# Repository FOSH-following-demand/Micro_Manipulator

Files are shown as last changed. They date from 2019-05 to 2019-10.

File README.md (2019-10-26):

# Micro Manipulator v2.0

Hi! we have a new design for the micromanipulator! check this out:

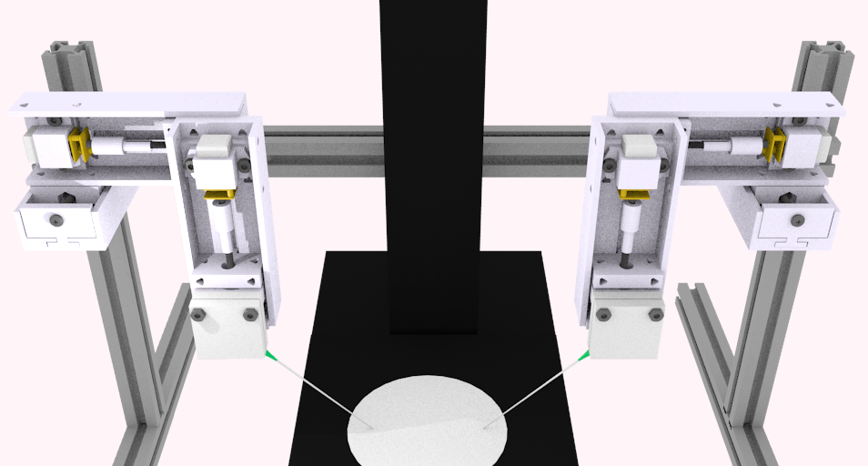
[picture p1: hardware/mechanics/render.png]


# 3D Printed parts

-Axis Base: This is the main component of each axis because it holds all other components.

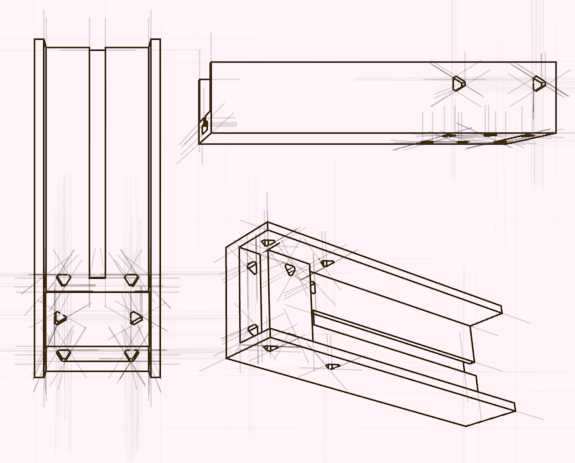
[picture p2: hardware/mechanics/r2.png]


You can find the STL file here: https://github.com/FOSH-following-demand/Micro_Manipulator/blob/master/hardware/mechanics/axis_base.stl

-Axis-Motor: It fixates the motor to the axis base

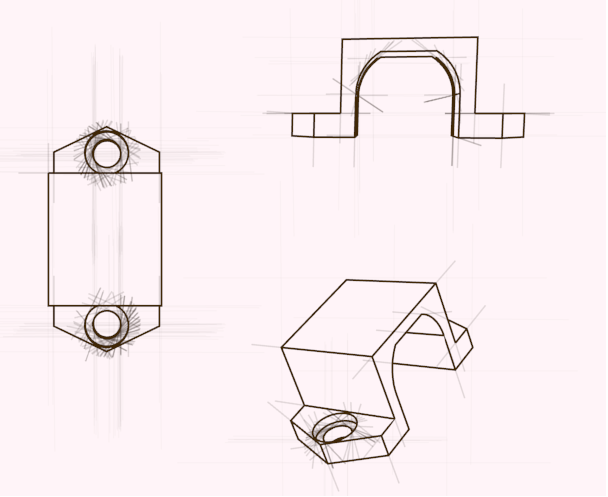
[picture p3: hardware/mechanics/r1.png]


You can find the STL file here: https://github.com/FOSH-following-demand/Micro_Manipulator/blob/master/hardware/mechanics/axis_motor.stl

-Axis TAP: The lid that closes the axis structure

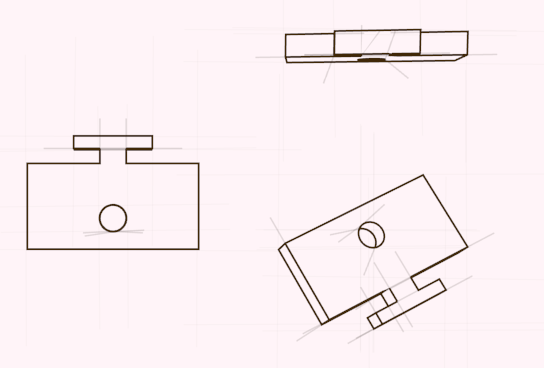
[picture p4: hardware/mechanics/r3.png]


You can find the STL file here: https://github.com/FOSH-following-demand/Micro_Manipulator/blob/master/hardware/mechanics/axis_tap.stl

-Axis Bolt A: One of the two pieces that when coupled turn rotational movement into linear one. 

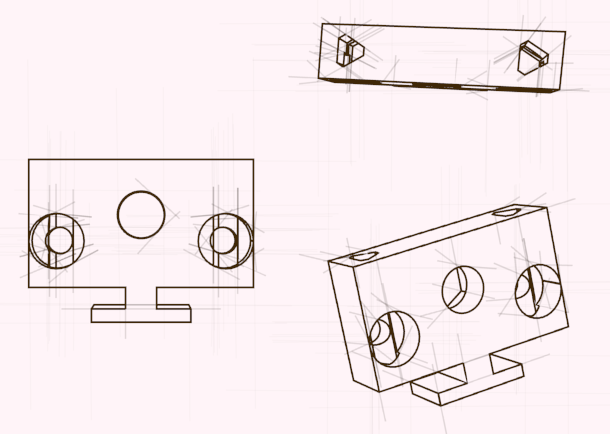
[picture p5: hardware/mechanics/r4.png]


You can find the STL file here: https://github.com/FOSH-following-demand/Micro_Manipulator/blob/master/hardware/mechanics/axis_bolt_a.stl

-Axis Bolt B: This piece complements axis bolt A to turn rotational movement into linear one 

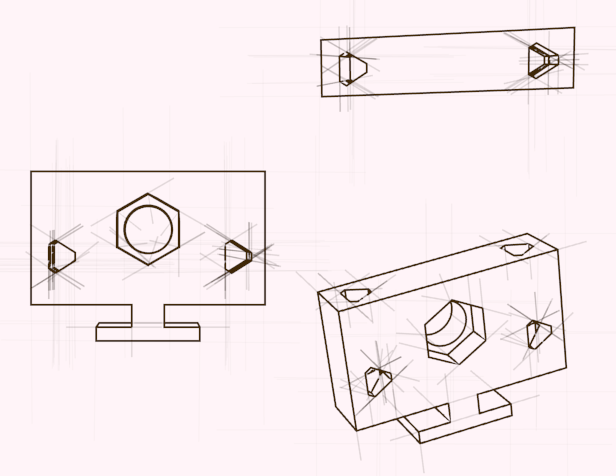
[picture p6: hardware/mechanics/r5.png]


You can find the STL file here:: https://github.com/FOSH-following-demand/Micro_Manipulator/blob/master/hardware/mechanics/axis_bolt_b.stl

-Prof X: THis piece will let you fit the axis to the aluminium profile 

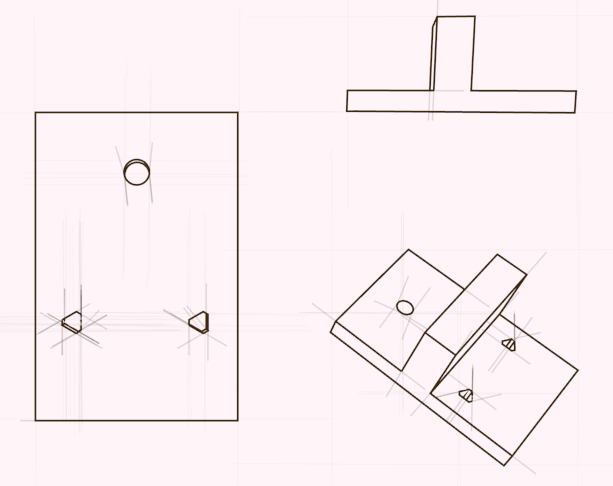
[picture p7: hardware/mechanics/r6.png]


You can find the STL file here: https://github.com/FOSH-following-demand/Micro_Manipulator/blob/master/hardware/mechanics/prof_x.stl

-Z needle A-B: These symmetric pieces will let you fit the needle to the Z axis 

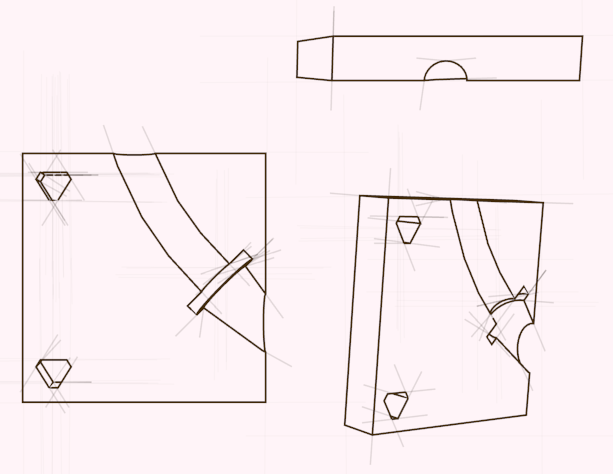
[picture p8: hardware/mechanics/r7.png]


You can find the STL files here:

https://github.com/FOSH-following-demand/Micro_Manipulator/blob/master/hardware/mechanics/z_jeringa_a.stl

https://github.com/FOSH-following-demand/Micro_Manipulator/blob/master/hardware/mechanics/z_jeringa_b.stl

# Parts assembly

- Building the Axis 

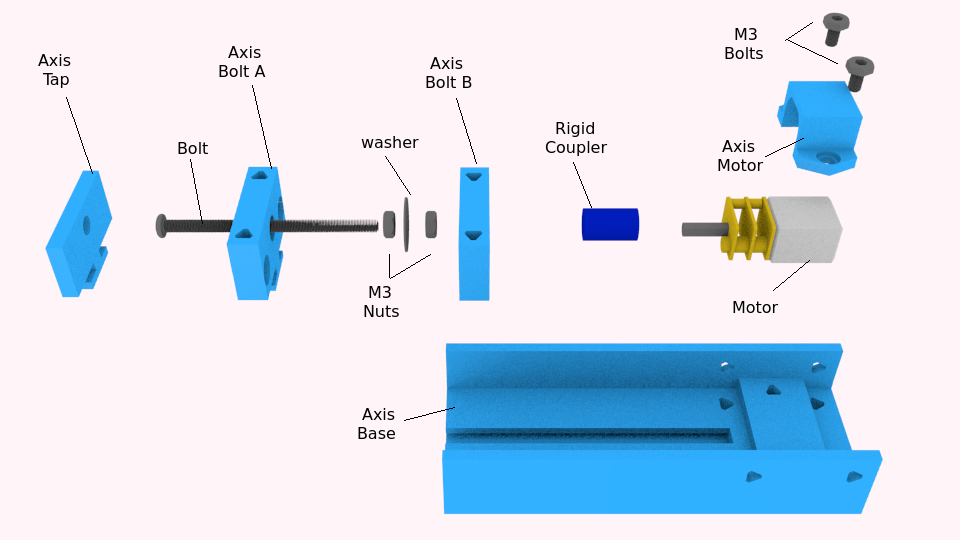
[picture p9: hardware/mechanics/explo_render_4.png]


- Joining the 3 axis with the aluminum profile

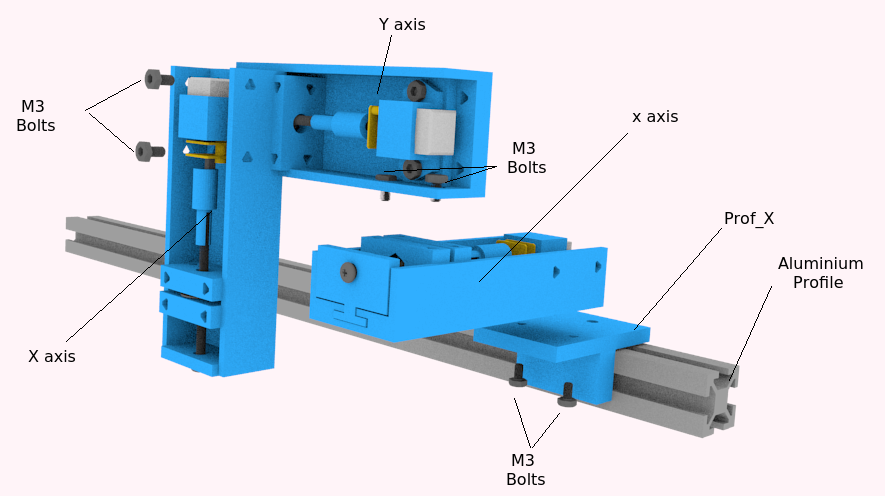
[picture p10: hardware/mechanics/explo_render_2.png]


- Placing the needle on the z axis

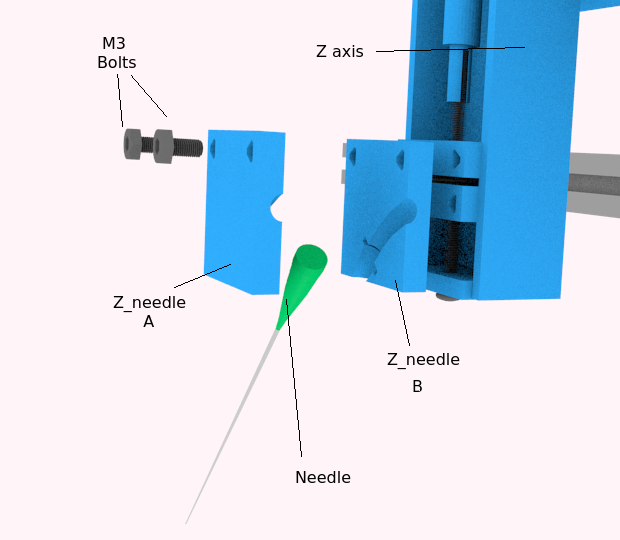
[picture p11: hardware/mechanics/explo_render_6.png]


Electronics:

Schematics here:

Programming here: 

Step by step [coming soon...]

# Micro Manipulator v1.0

We are "Peru team". We want to build an open source micromanipulator. 

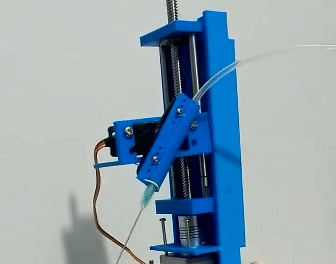
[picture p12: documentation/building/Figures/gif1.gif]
 

# Background 
This equipment lets the user manipulate things in a microscopic level. Common uses include cell manipulation and is also quite common in reproductive biology for Intracytoplasmic Sperm Injection (ICSI)-

# Commercial micromanipulators
| Brand         | Code          |Origin             |  Name         | Notes - relevance | 
| ------------- | ------------- | ----------------- | -------------- | --------------    |
| Narishige     | MMO-203       | Japan             | Three-axis Oil Hydraulic Micromanipulator|   |
| Narishige     |   MKT-I       |   Japan           |    Four-axis Hanging Joystick Oil Hydraulic Micromanipulator|    |

# Other Open source micromanipulators
| Project name  | URL           | Active/Not active | Notes - relevance |
| ------------- | ------------- | ----------------- | -------------- |
| Parametric 3 axis manipulator | https://www.thingiverse.com/thing:239105 | Active |  Micromanipulator e.g. for use in a laboratory setting |
| Micromanipulator  | https://www.thingiverse.com/thing:923865 | Active |  3D printable 3 axis |

# Proof of concept

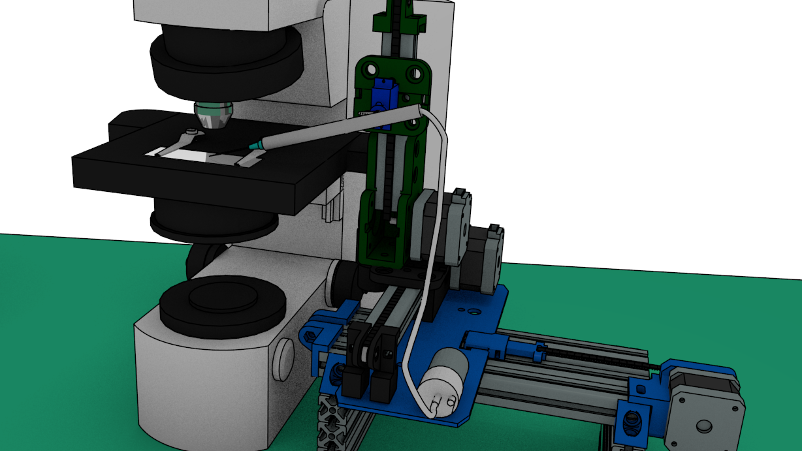
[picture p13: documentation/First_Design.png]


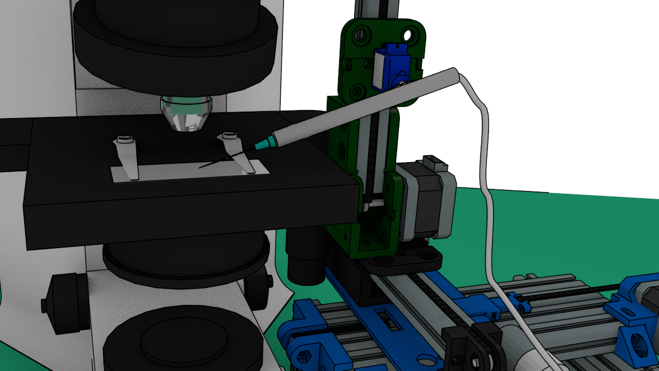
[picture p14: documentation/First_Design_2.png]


# First advances

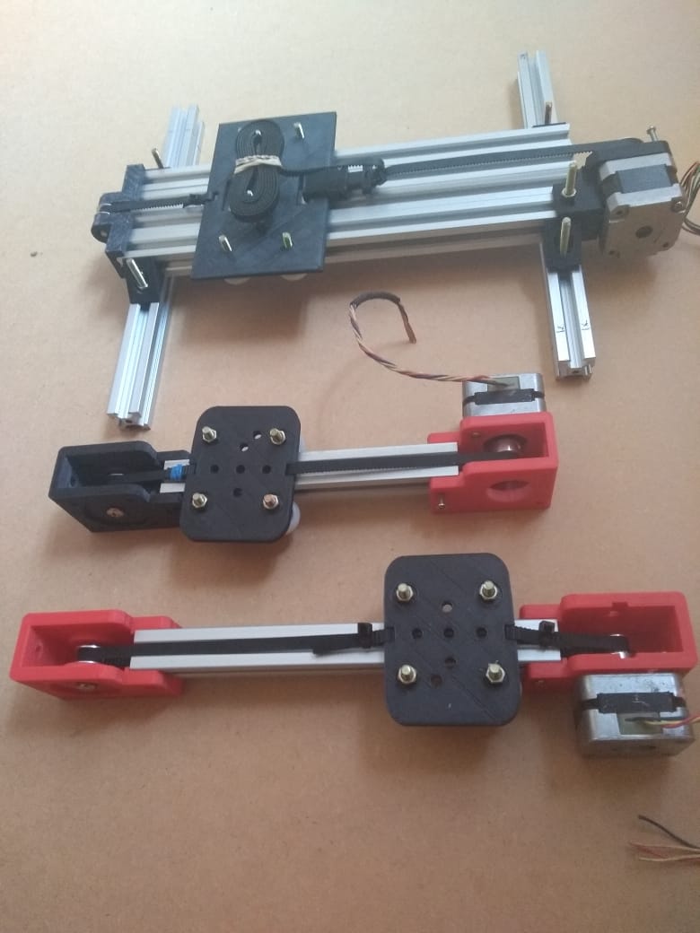
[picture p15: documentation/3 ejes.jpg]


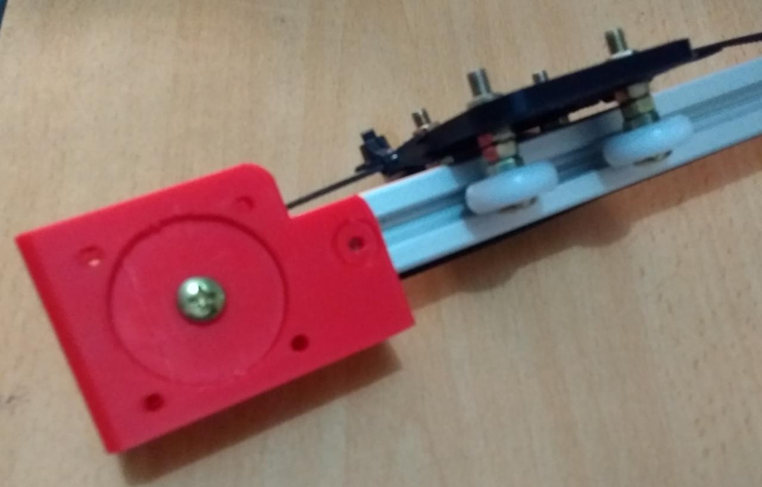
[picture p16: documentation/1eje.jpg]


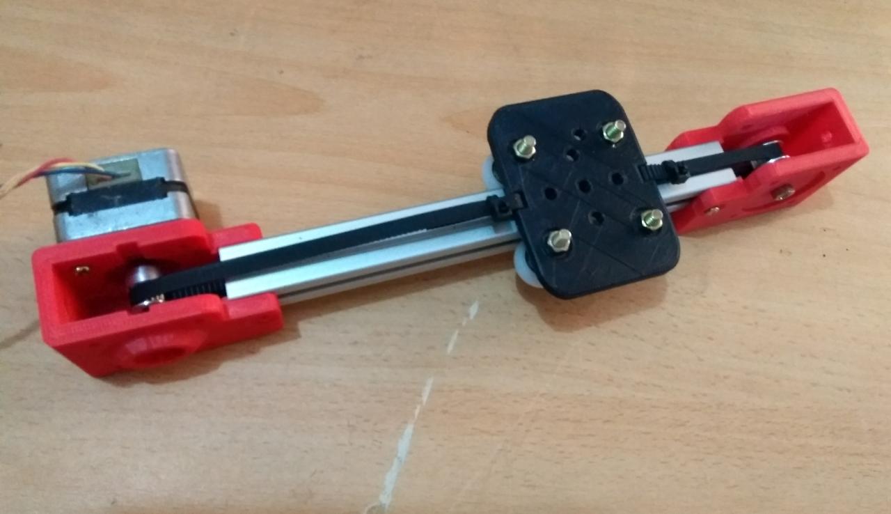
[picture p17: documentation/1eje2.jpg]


# Final version

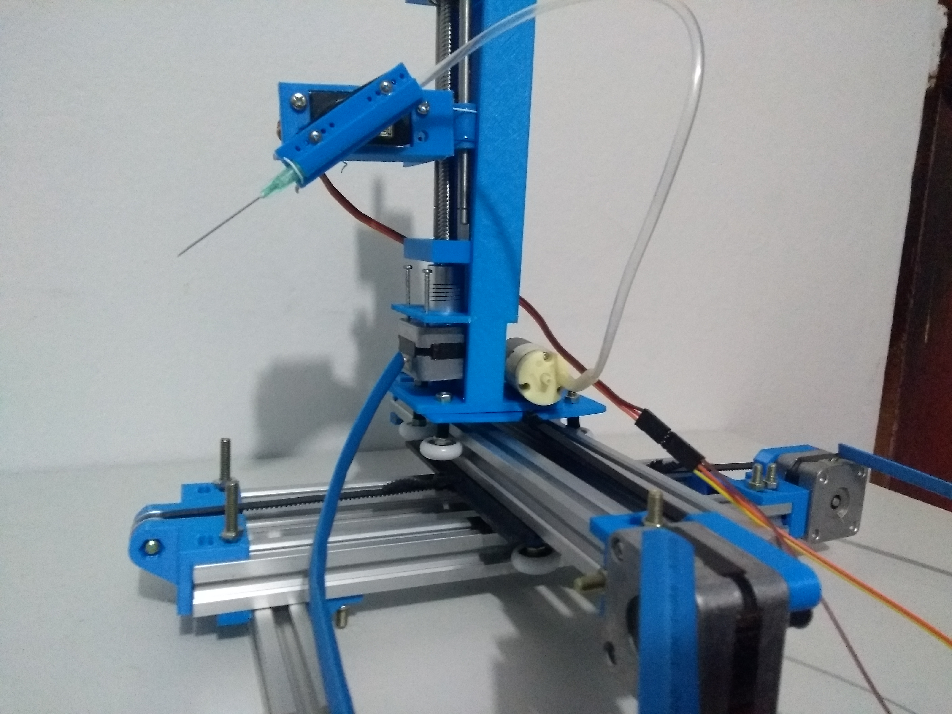
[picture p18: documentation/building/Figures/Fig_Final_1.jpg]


# Demo

IMAGE ALT TEXT HERE (https://www.youtube.com/watch?v=eaM0OVvJmCg)

# DC Micro Pump 

IMAGE ALT TEXT HERE (https://www.youtube.com/watch?v=rROfGqbosEs)

# App Tests

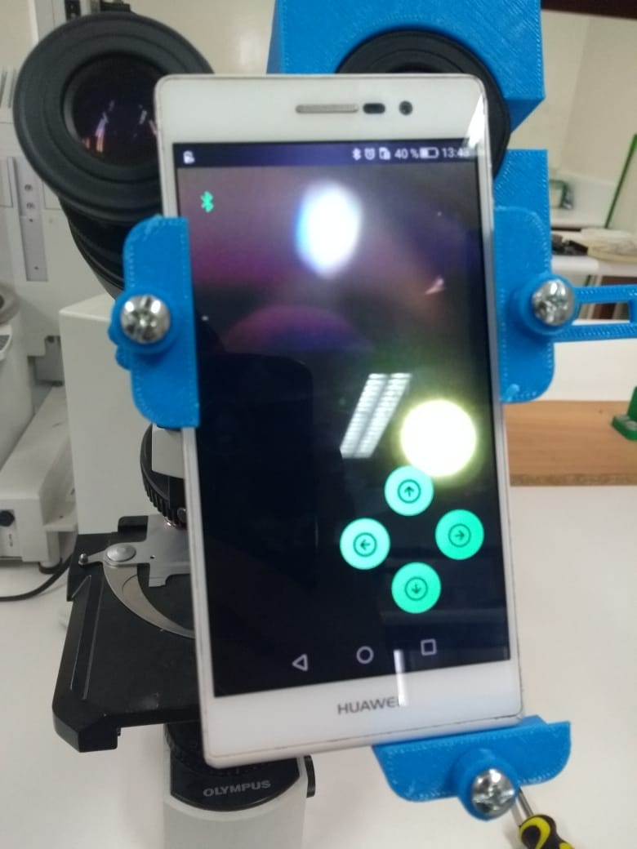
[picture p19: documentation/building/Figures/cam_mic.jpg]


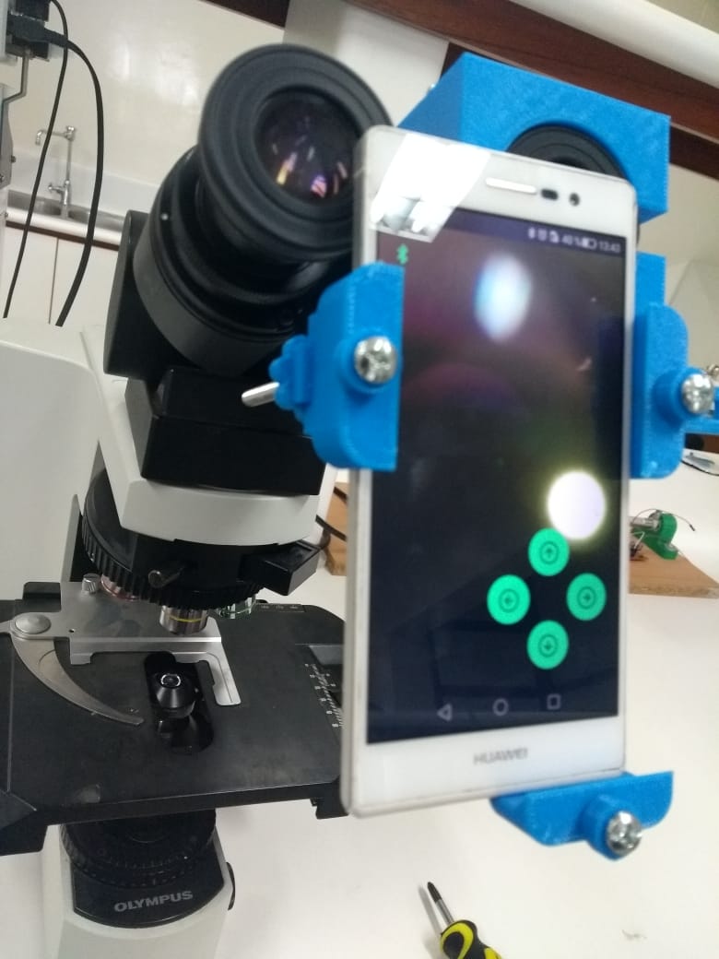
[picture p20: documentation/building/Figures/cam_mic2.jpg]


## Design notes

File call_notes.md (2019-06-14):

## notes for the calls:

### Call on June 14th

Note taker: Andre

Hectic week, international travels, master thesis defense! So this project was left a bit to the side (understandably so!).
Still the team has made progress. and shared it during the call.

The prototype is complete! 
There is a problem with the stability of the Z axis, it vibrates when operated.

Suggestions: 
- build an U shaped part and put on top of Z axis,
- build triangularshapes and fix then to the side of the profile.

Another issue, there is soee wobble in the wheel/profile junction.  

Suggestions:
- use springs to keep the junction under tension.

For next week:
- Wednesday June 19Th
Step by step guide on documentation.

### Call on June 4th 

Note taker: Andre

Paypal transfer takes 5 working days, so the transfer will only be available tomorrow.
But they have been buying parts already.

Updates:

 - They assembled part of the axes. they were based on 3D printers and open bricks?. Some parts had to be adapted so the whole
 thing would fit inside the microscope. The main problem is the height. 

Struggles:
The height is an issue, since microscopes have a very high variation. 
the designs are built with Blender.
One idea is to use arrays in Blender so that people can easily change the size (they are predefined though).

What's next:
- put micro servo on the Z axis to engage the syringe. 
- from commercial manipulator: three wheels are used for each axis
- bill of materials and building instructions

- to calibrate: take a picture from each point and set that position on software. Go to another position and come 
back to the previous position to see how much error is there.

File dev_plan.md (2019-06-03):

# Development plan

Use this file to store your plan for the program. What are you going to do, in which order? 

| Week        | Activities           | Who           |
| ----------- | -------------------- | ------------- |
| 1           |   Background check for existing Open source designs     |   Dulce & Jean Pierre            |
| -           |   Work plan establisment   |   All            |
| 2           |   Proof of concept (3D design)     |        Jean Pierre       |
| -           |  List of supplies  |        Dulce & Jean Pierre   |
| 3           |  First purchases   |       Jean Pierre & Anthony      |
| -           |  Assemble each carridge in axes       |       Jean Pierre      |
| 4           | Motor calibration             |        Jean Pierre       |
| -           | Try out actuators in Z axis and control system (wheels and joystick)   |    Jean Pierre           |
| 5           |  Software control development     |  All           |
| -           |  GUI Development     |        Anthony       |
| 6           |                      |               |
| 7           |                      |               |
| 8           |                      |               |

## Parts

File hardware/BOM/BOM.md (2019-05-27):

#### Create BOM files for the equipment

We recommend creating different files:

<br>

- Electronic_BOM.csv: table containing all the integrated circuits(IC) 

<br>

| Reference | Quantity  | Description | Manufacturer  |MPN| manufacturer_1  |MPN_2| manufacturer_3  |MPN_4|
|---|---|---|---|---|---|---|---|---|
| Arduino Mega 2560  | 1  | 	Microcontroller board   | - | - | - | - | - |	- |	

<br>

- Mechanical_BOM.csv: Table containing all the mechanical parts necessary to build the equipment. 

<br>

| Part name| Function  | Quantity  |  obs.  |supplier|supplier number|link|
|---|---|---|---|---|---|---|

<br>

- Tools_BOM.csv: table containing all tools used for the build.

<br>

| Part name| Function  | Quantity  |  obs.  |supplier|supplier number|link|
|---|---|---|---|---|---|---|
| 3D Printer | To build the pieces of equipment  | 1  | - | - | - | - |

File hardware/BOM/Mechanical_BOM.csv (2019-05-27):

Part name | Function | Quantity | obs. | supplier | supplier number | link
Nema 17 | Stepper motor for each axis | 3 | - | - | - | -
Solid wheel | Used to move the plates | 12 | - | - | - | -
Timing Pulley | Used to move the plates | 3 | - | - | - | -
Tooth Pulley | Used to move the plates | 3 | - | - | - | -
Timing Belt x1000mm | Used to move the plates | 5 | - | - | - | -
T-SLOT Aluminium Profile 20x20 x1000mm | Used as frame for the machine | 4 | - | - | - | -
Servomotor SG-9G | Used for rotate the noodle | 1 | - | - | - | -
Noodle | Used for collect the sample | 1 | - | - | - | -
Syringe | Used for collect the sample | 1 | - | - | - | -
M3 Hex Screw | Used for holding motors | 20 | - | - | - | -
M3 Hammer Nut | used for holding motors | 20 | - | - | - | -
Printed Parts | Frames for fit the pieces | x | - | - | - | -

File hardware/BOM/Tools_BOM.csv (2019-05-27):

Part name | Function | Quantity | obs. | supplier | supplier number | link
3D Printer | To build the pieces of equipment | 1 | - | - | - | -
ABS Filament x 1Kg | Material for the 3D printer | 2 | - | - | - | -

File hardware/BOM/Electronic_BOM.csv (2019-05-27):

Reference | Quantity | Description | Manufacturer | MPN | manufacturer_1 | MPN_2 | manufacturer_3 | MPN_4
Arduino Mega 2560 | 1 | Microcontroller board |  | - | - | - | - | -
Driver Motor A4988 | 4 | Driver for stepper motors |  | - | - | - | - | -
CNC Shield | 1 | Shield for arduino |  | - | - | - | - | -
Endstop | 6 | Switch to detecto end of rail |  | - | - | - | - | -
Power Supply | 1 | Supplies power to the machine | - | - | - | - | -

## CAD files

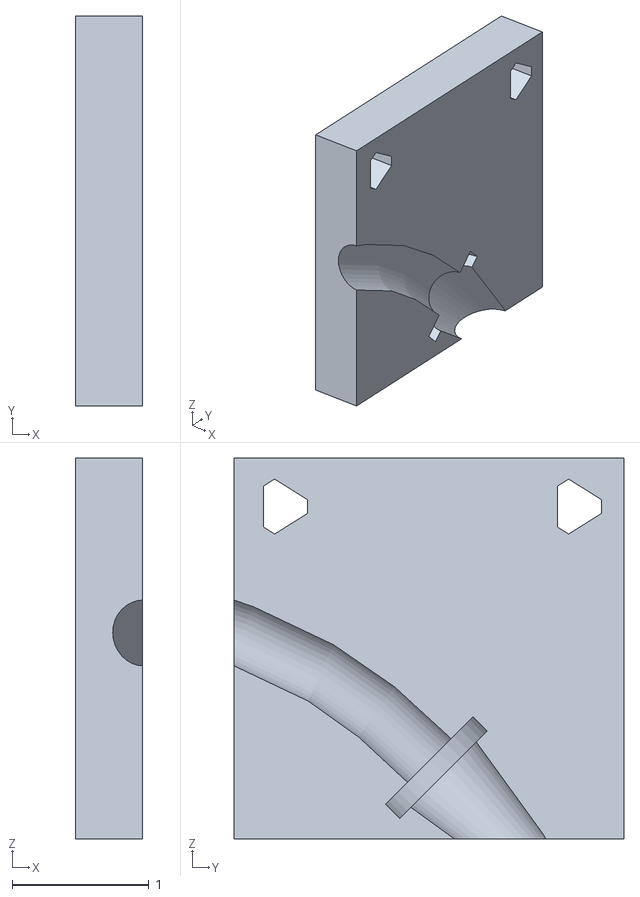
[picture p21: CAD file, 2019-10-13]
hardware/mechanics/z_jeringa_b.stl
0.49 x 2.85 x 2.78

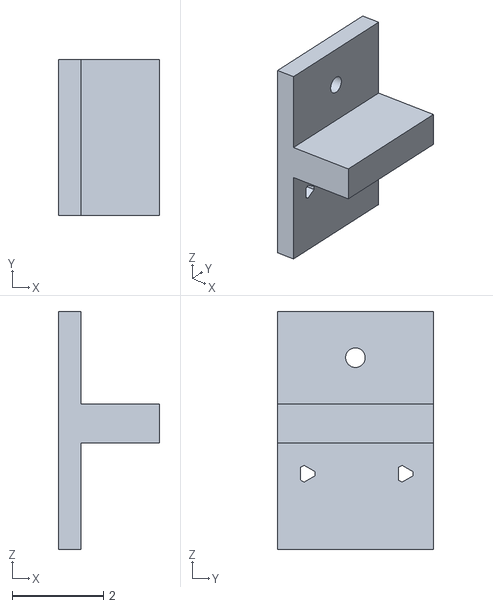
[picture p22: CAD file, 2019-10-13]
hardware/mechanics/prof_x.stl
2.22 x 3.43 x 5.22

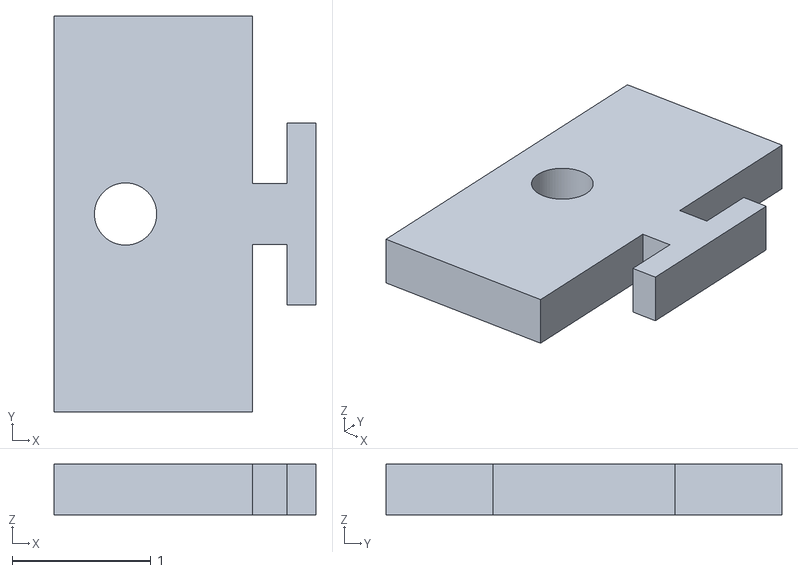
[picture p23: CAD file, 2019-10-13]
hardware/mechanics/axis_tap.stl
1.89 x 2.86 x 0.367

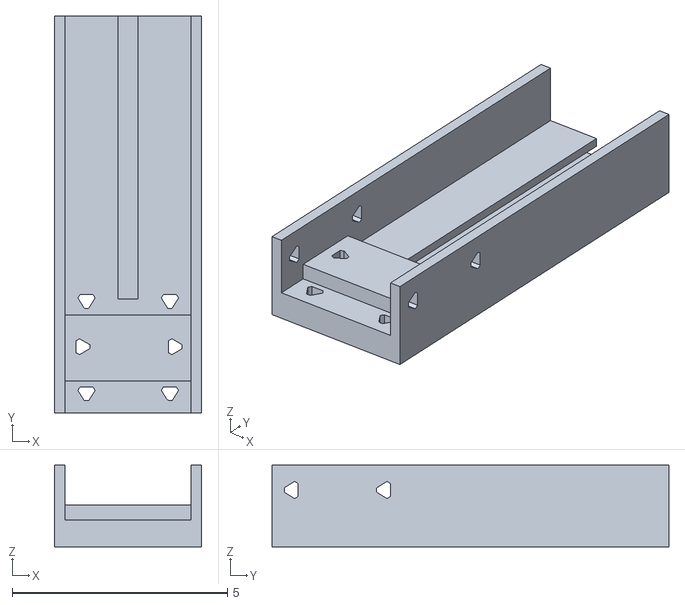
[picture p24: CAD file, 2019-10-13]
hardware/mechanics/axis_base.stl
3.43 x 9.22 x 1.90

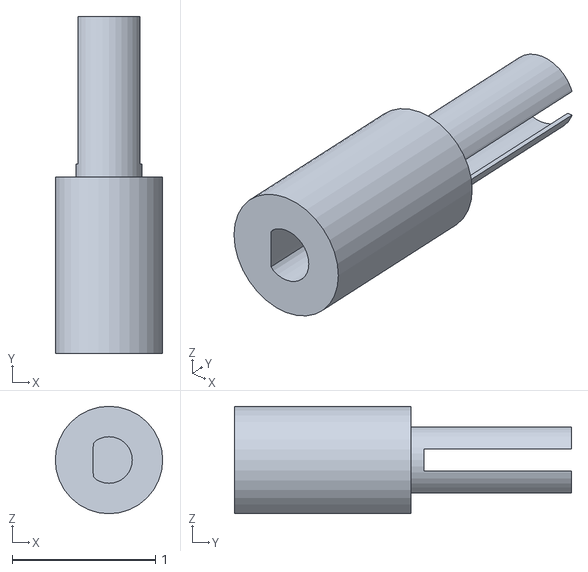
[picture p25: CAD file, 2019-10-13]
hardware/mechanics/axis_coupler.stl
0.749 x 2.35 x 0.749

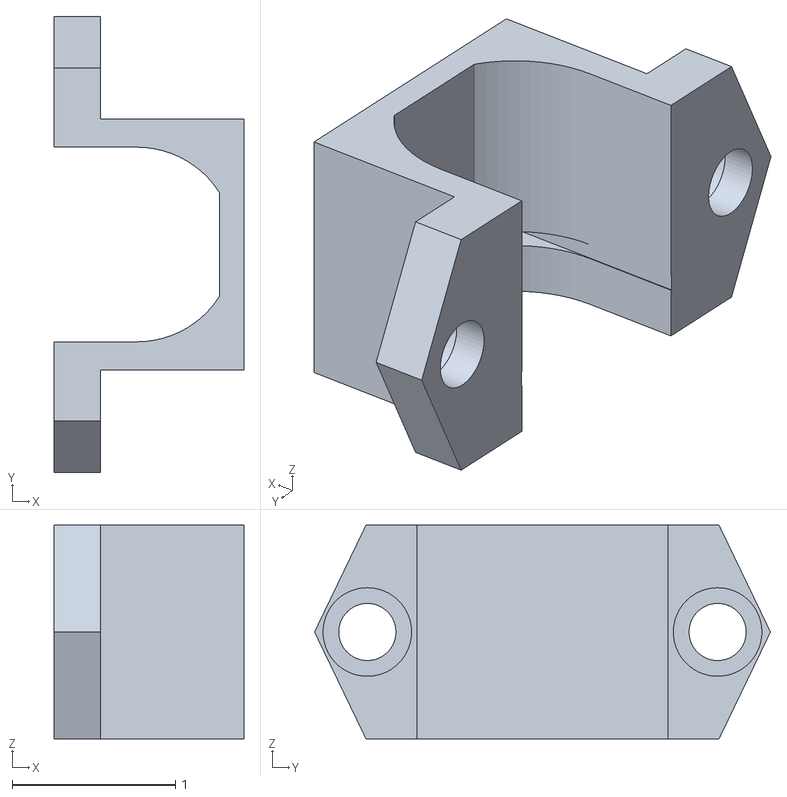
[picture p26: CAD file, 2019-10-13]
hardware/mechanics/axis_motor.stl
1.16 x 2.80 x 1.31

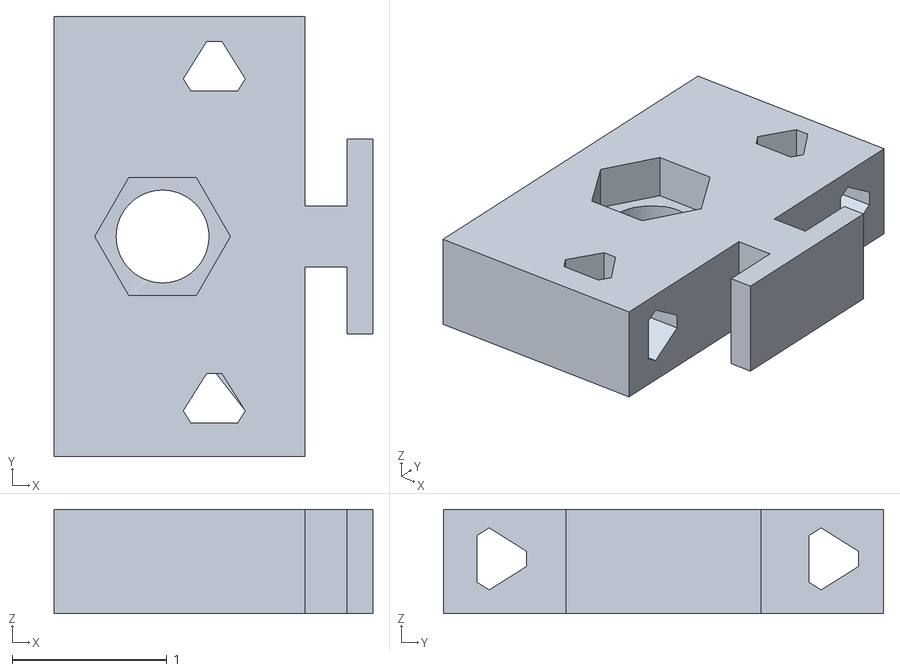
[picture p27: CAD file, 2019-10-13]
hardware/mechanics/axis_bolt_b.stl
2.06 x 2.85 x 0.675

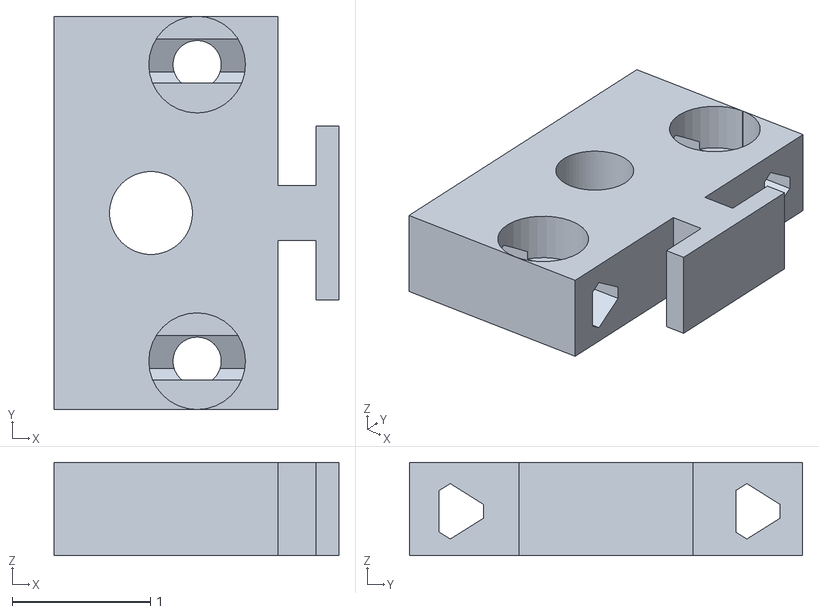
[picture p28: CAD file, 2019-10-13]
hardware/mechanics/axis_bolt_a.stl
2.06 x 2.85 x 0.675

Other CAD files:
hardware/mechanics/z_jeringa_a.stl

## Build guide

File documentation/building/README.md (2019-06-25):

## Assembly Instructions (English) ##
( Versión en Español [aquí](https://github.com/FOSH-following-demand/Micro_Manipulator))

**1. Building the X axis plate:**

Mechanical parts:

- 23mm nylon wheels - 4 pieces               
- M5x30mm - 4 pieces (Bolt and hammer nut)   
- M3x25mm - 2 pieces (Bolt and hammer nut)            

3D printed parts 
- 4 cylinders         
- Base of the X axis  
- Y axis support     

First, we take one of the M5x30mm bolts and put it in a nylon wheel and adjust it with its corresponding nut 

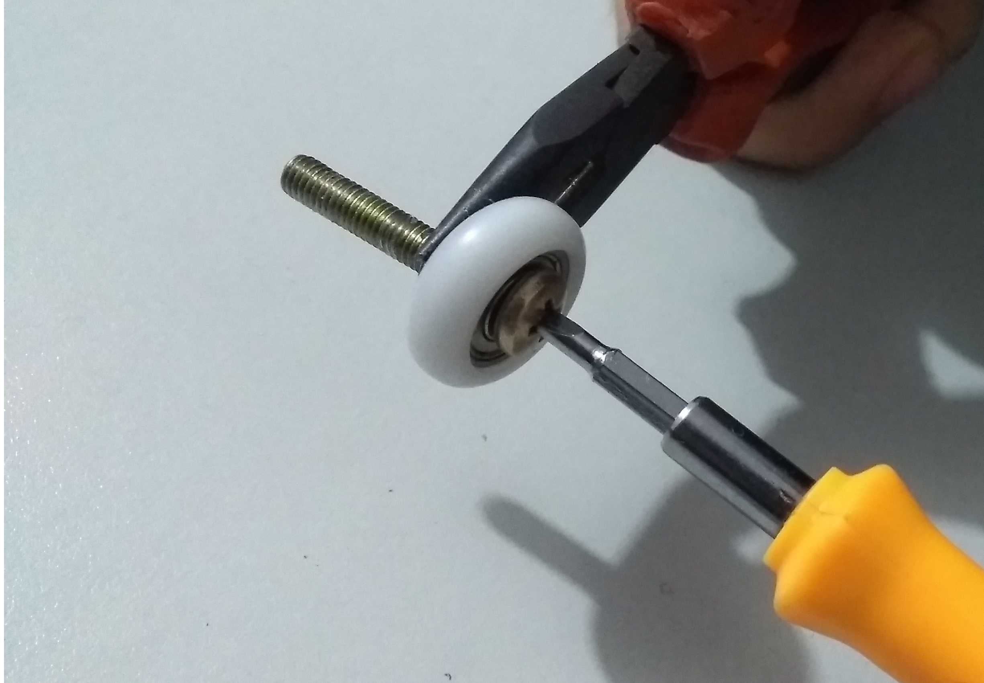
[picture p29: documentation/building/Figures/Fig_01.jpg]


We take the printed cylinders and put it after the nut 

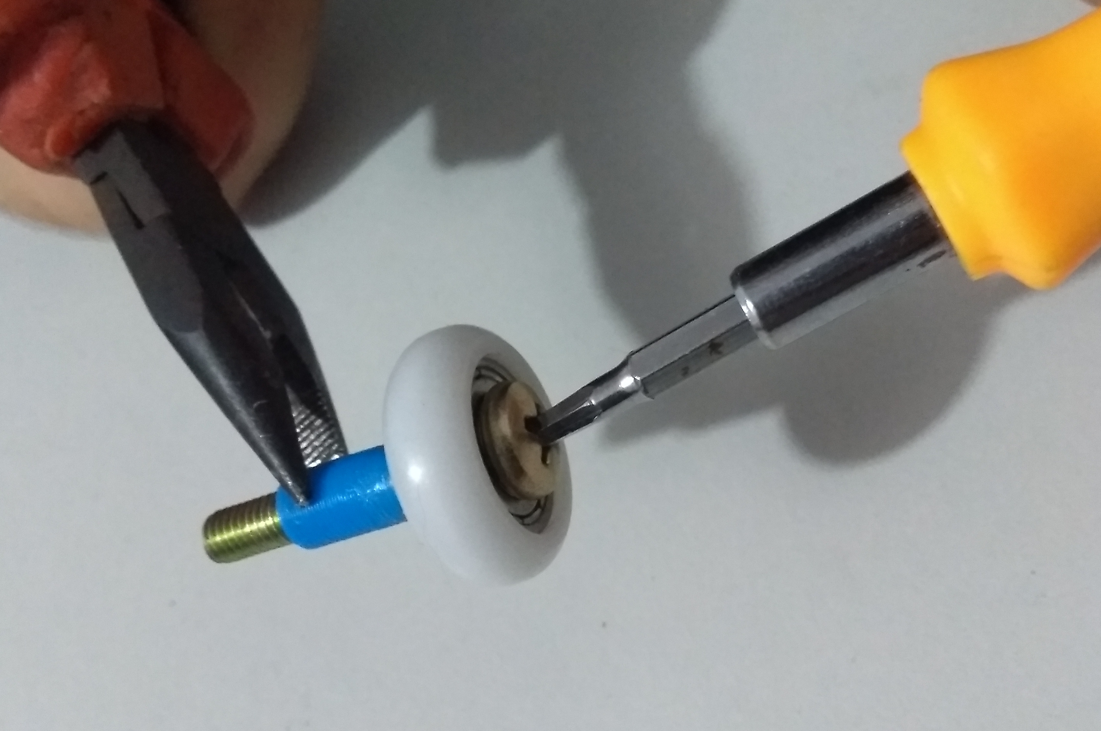
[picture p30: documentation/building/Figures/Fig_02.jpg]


Then, we insert this piece inside one of the wholes of the base of the X axis plate, and repeat for the 4 wheels 

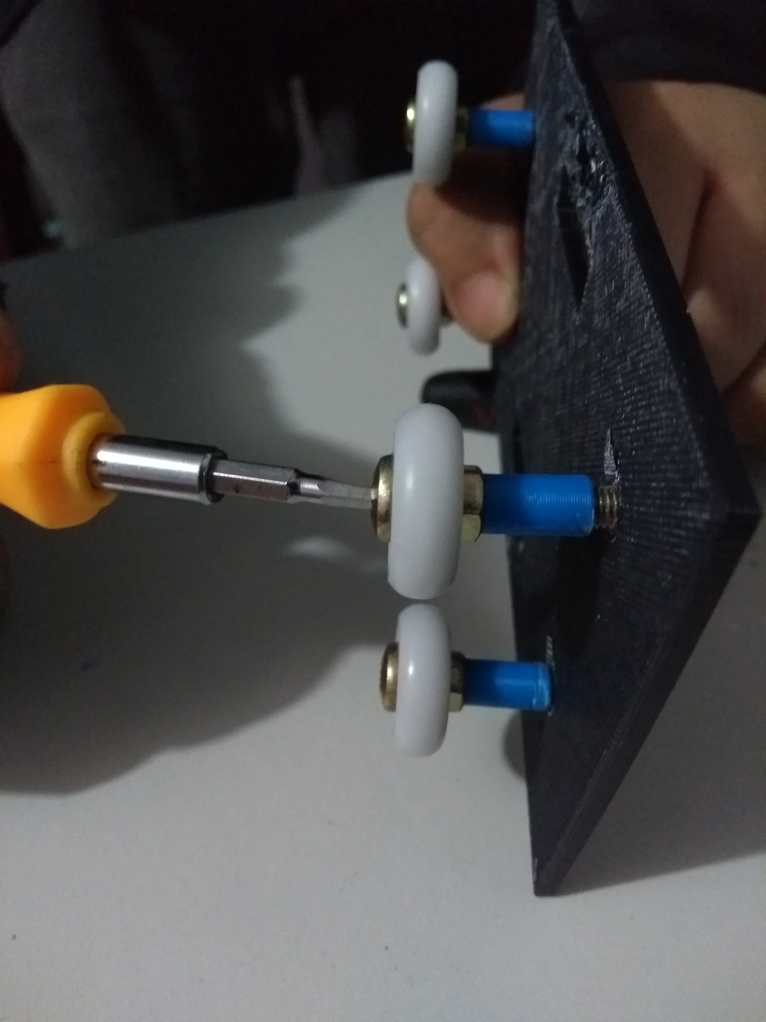
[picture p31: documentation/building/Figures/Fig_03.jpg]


We adjust it with his corresponding nut 

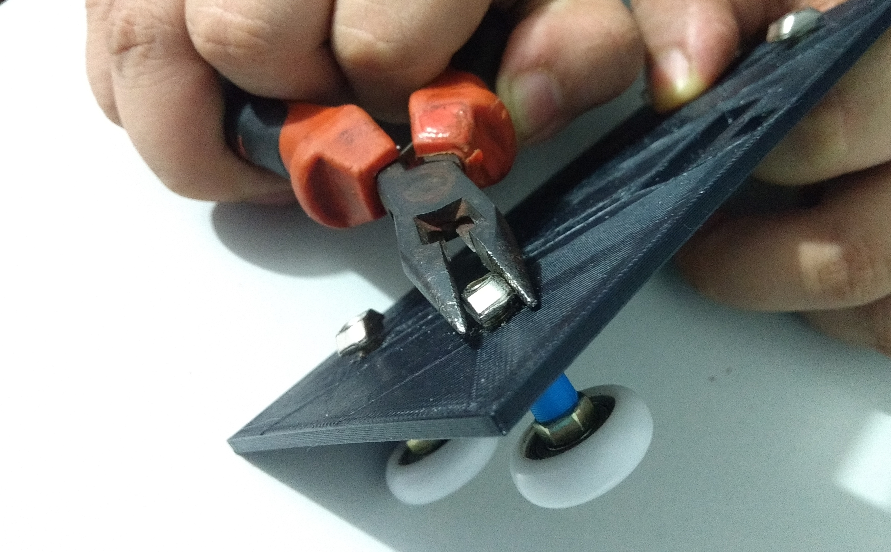
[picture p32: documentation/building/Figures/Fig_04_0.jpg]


we introduce the 2 profiles in the nuts that protrude from the plate
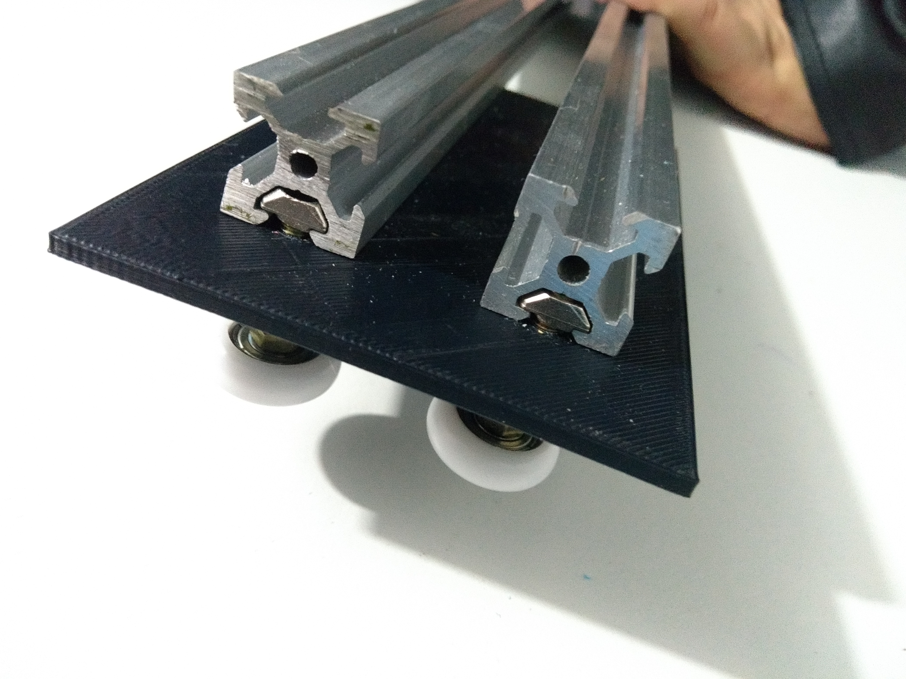
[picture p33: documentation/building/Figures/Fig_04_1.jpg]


we adjust the screws from the other side of the nylon wheels


**2. Building the X and Y axis:**

Mechanical parts:

- 6 aluminium profiles T-SLOT ( 2 of 25cm size and 4 of 30cm size)
- 1 NEMA 17 stepper motor 
- 1 belt of 50cm 
- 1 timing pulley 
- 4 angles for profiles 
- M3x10mm - 2 pieces (Bolt and hammer nut) 
- M5x10mm - 8 pieces (Bolt and hammer nut) 
- M5x30mm - 2 pieces (Bolt and hammer nut) 

3D printed parts:

- Motor support 
- Fit for belt 
- Right adjuster pulley and profile 
- Left adjuster pulley and profile 

We begin by putting one of the 30cm-profiles and put the hammer nut with one of the angles as shown in the figure

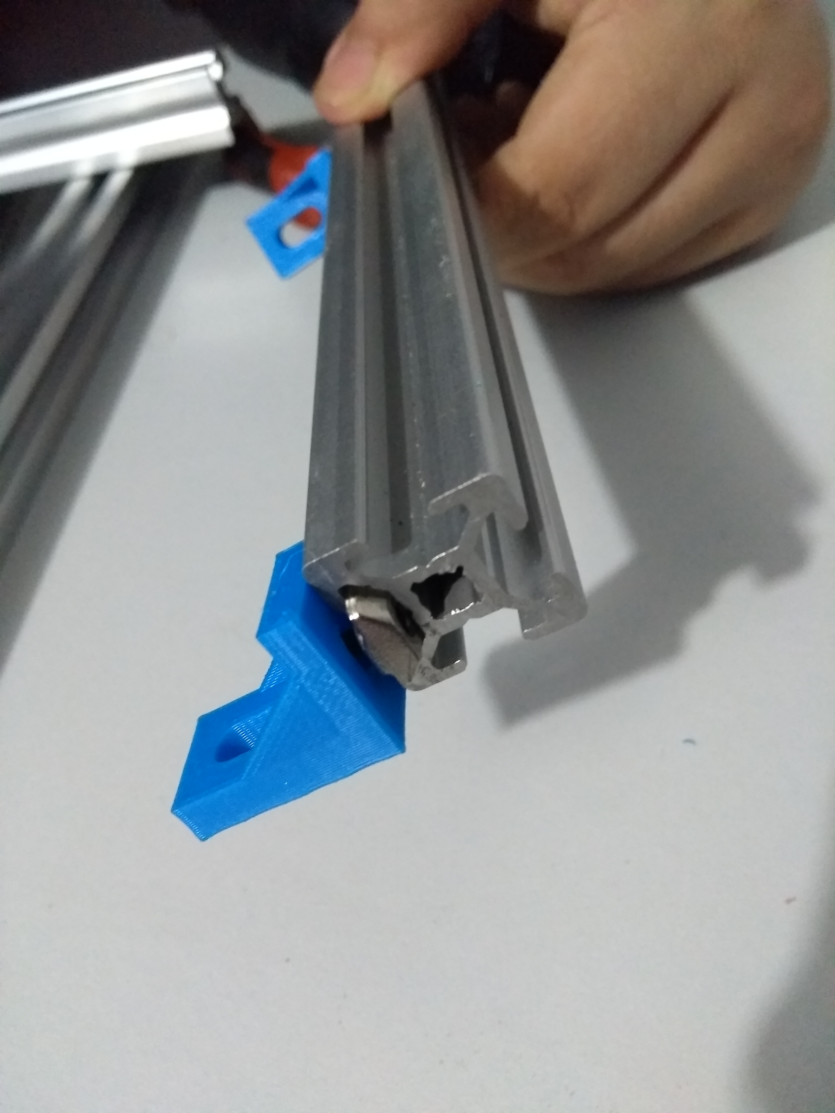
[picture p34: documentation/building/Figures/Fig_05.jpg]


We adjust the nut alongside the angle and repeat the last step with other nut in the other extreme of the profiles and adjust with the corresponding bolt

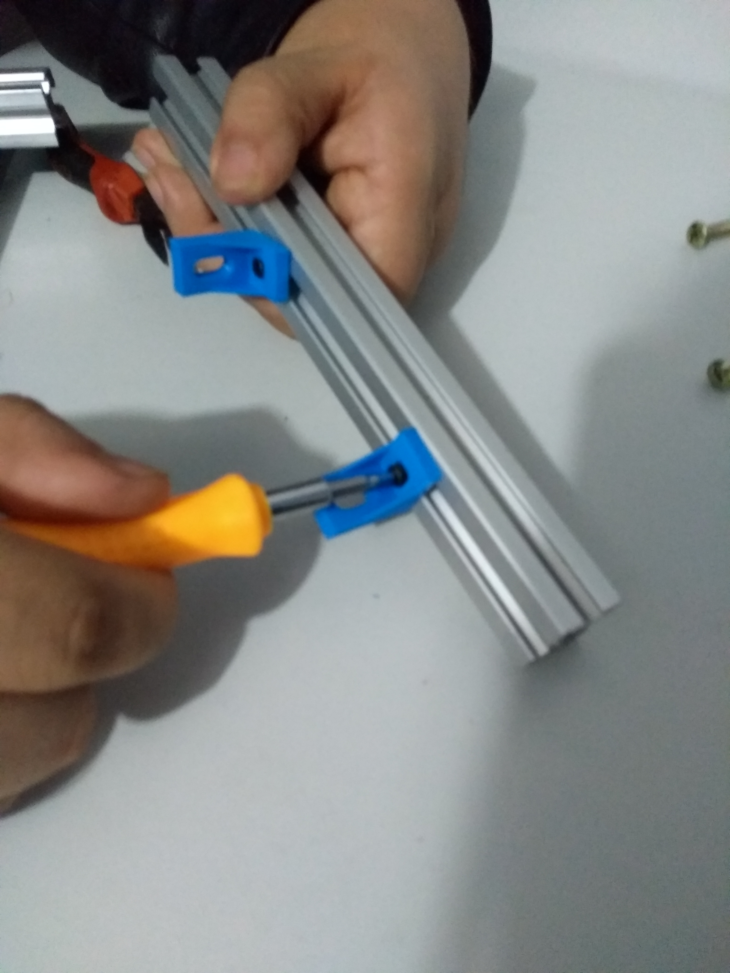
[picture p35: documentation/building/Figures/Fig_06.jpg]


Now we must align this piece with 2 profiles of 25cm and adjust them with bolts

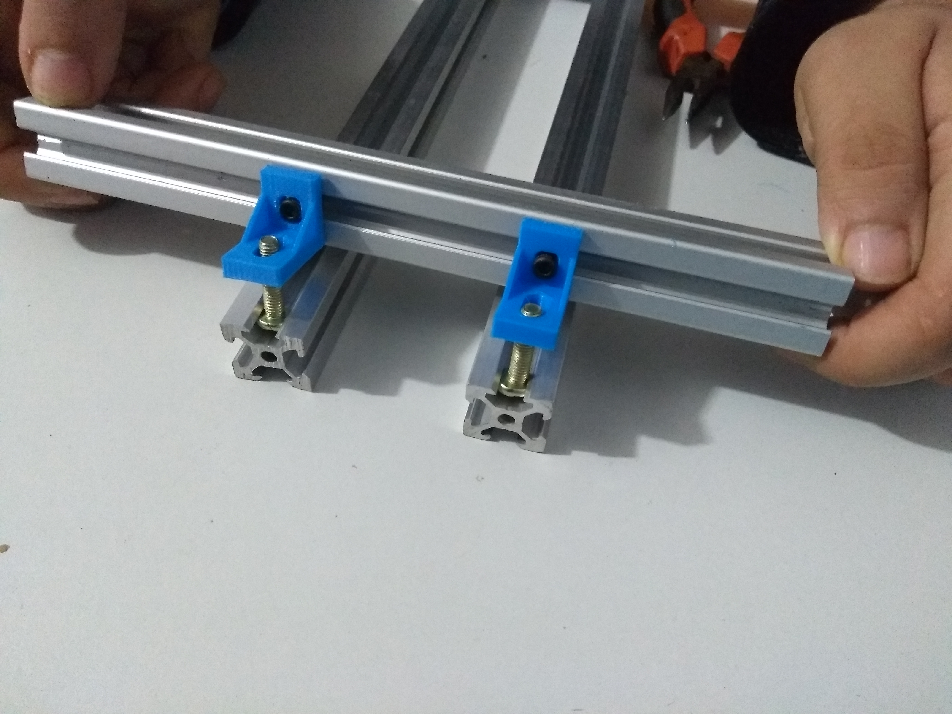
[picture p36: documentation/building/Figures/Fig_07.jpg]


we adjust with nuts

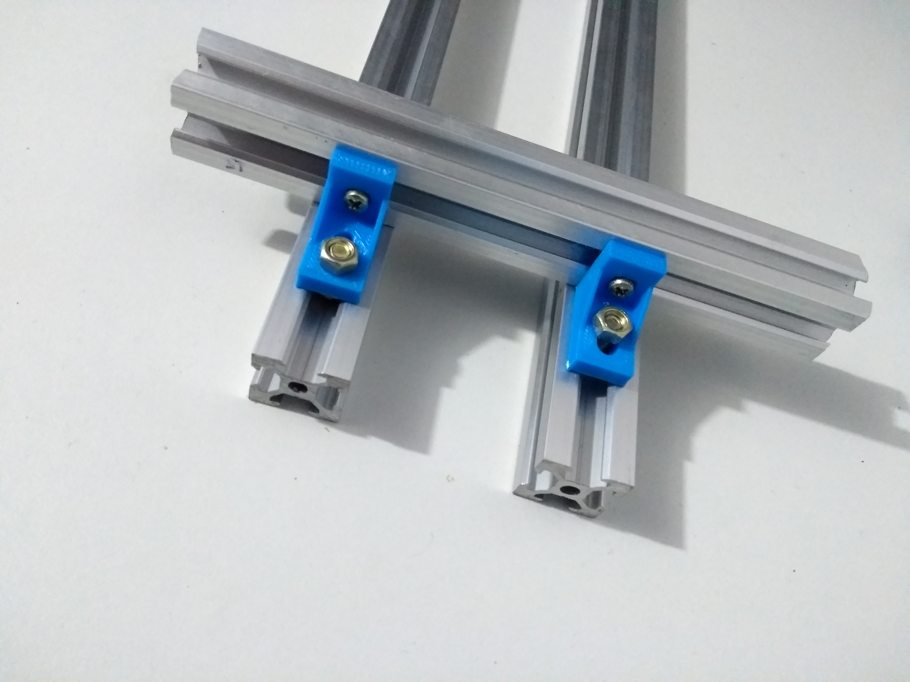
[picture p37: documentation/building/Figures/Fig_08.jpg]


we use a 3d printed profile separator and put the bolt with the hammer nut

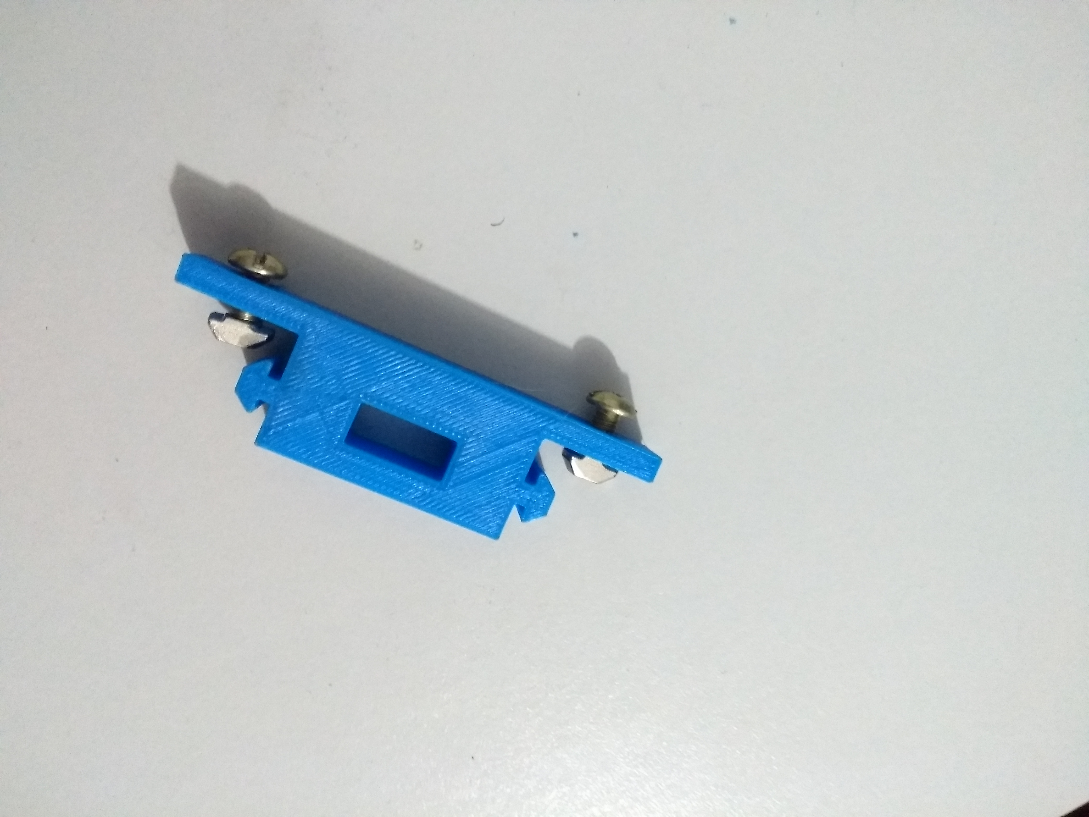
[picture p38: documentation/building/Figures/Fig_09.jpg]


introduce this profile separator between the two profiles

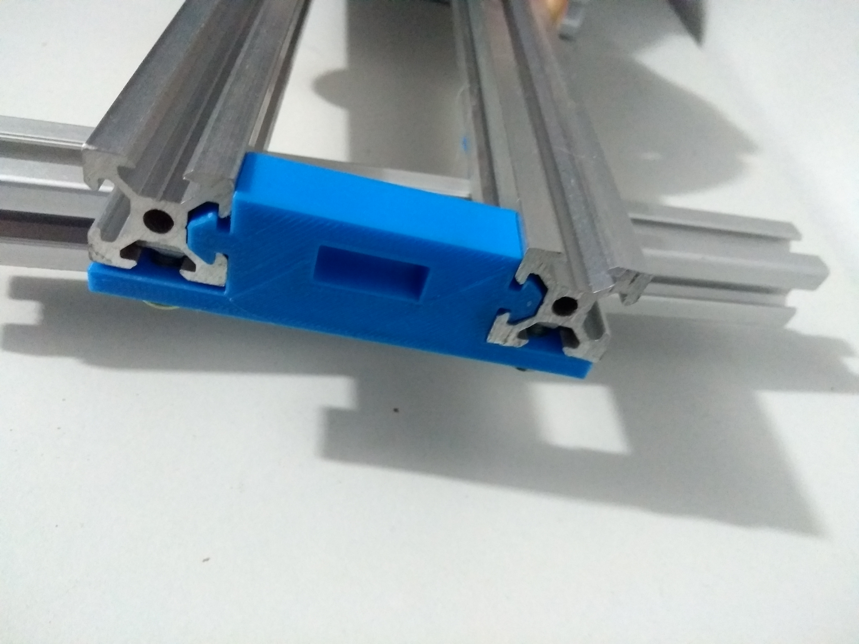
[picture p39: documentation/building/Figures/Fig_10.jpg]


we turn the pieces and adjust with the bolt

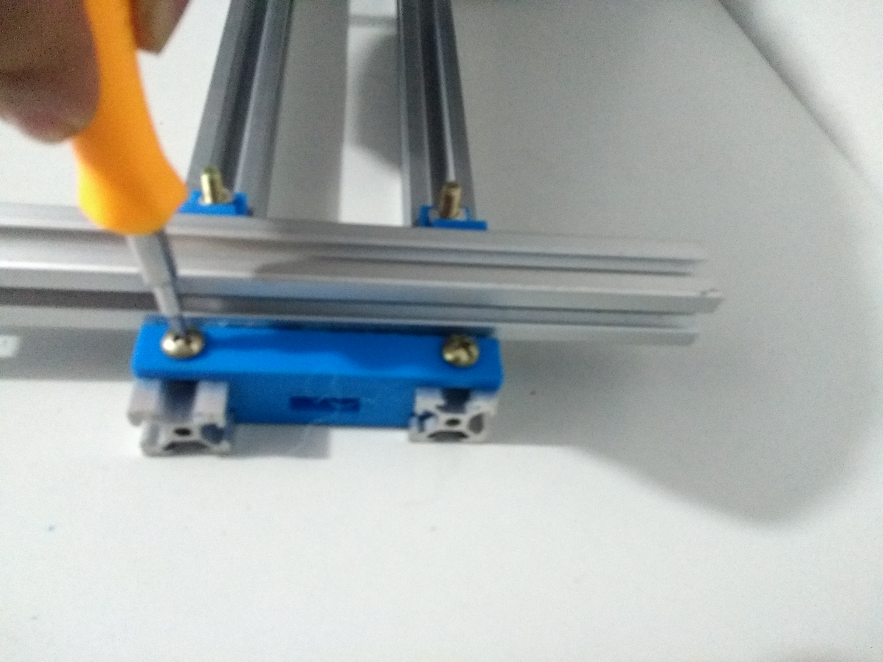
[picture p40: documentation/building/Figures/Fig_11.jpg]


Likewise, we repeat the steps for the other side of the profile

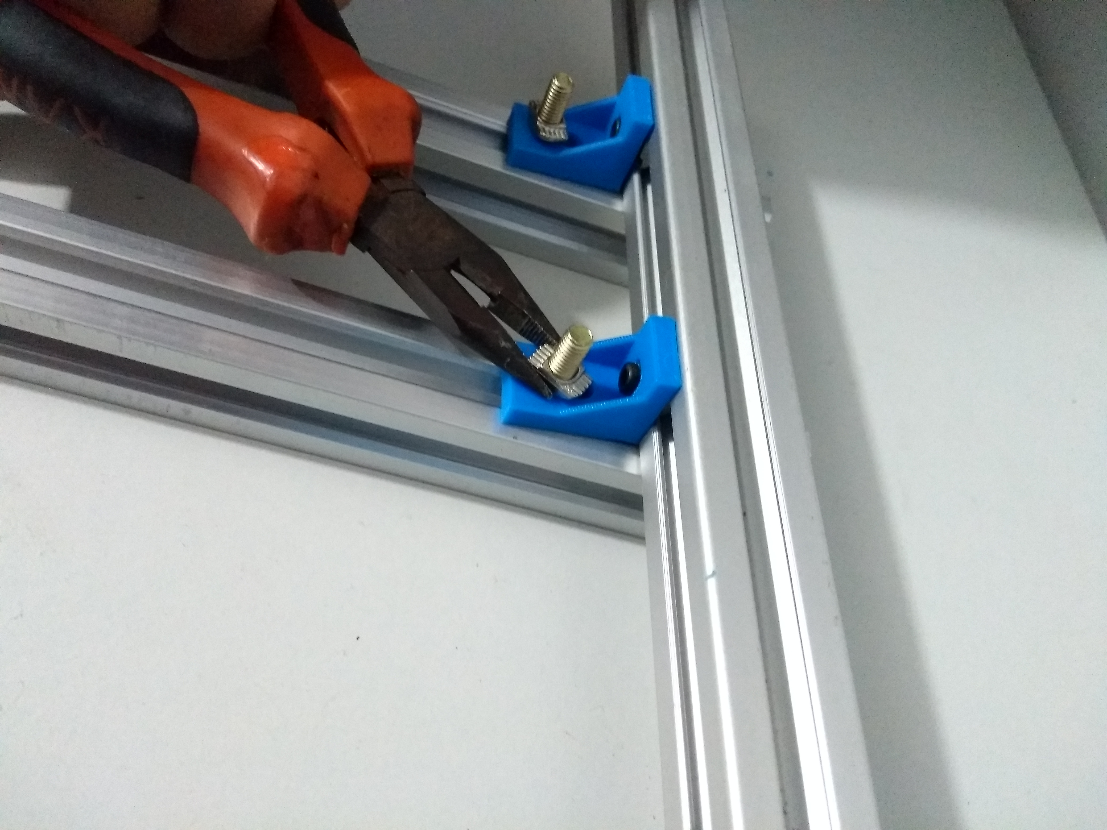
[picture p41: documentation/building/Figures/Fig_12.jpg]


Then, we enter the plate of the X axis previously assembled on the rail of profile X

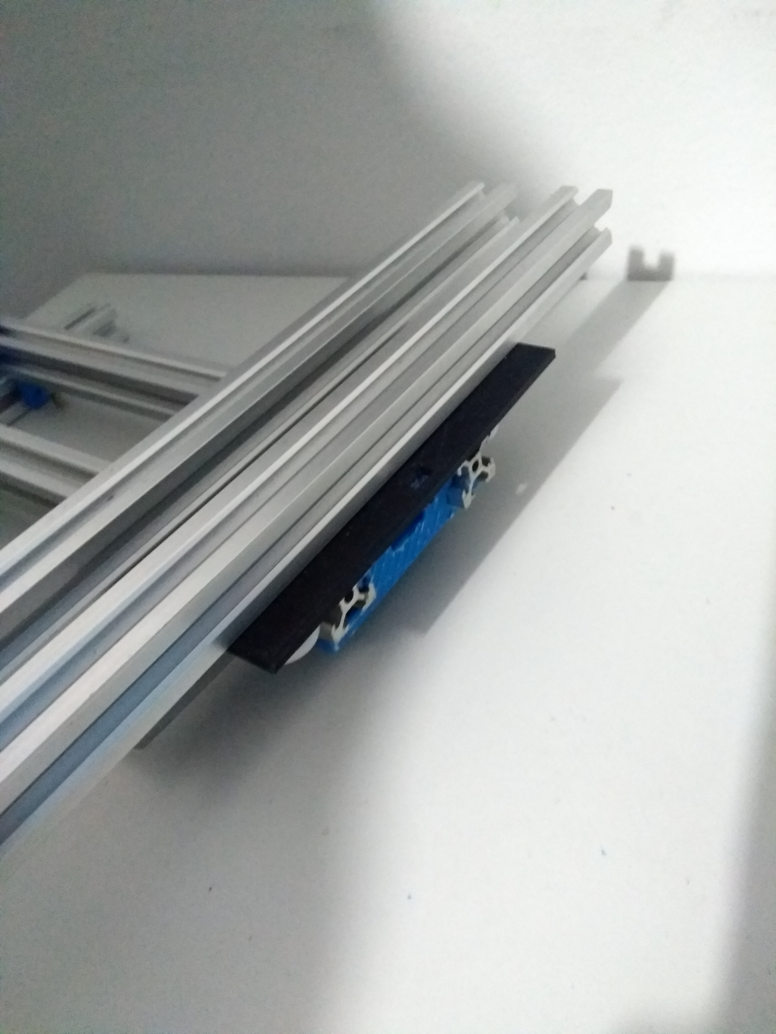
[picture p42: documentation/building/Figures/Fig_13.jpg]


we will use now, the 3d printed left and right belt adjuster with nuts

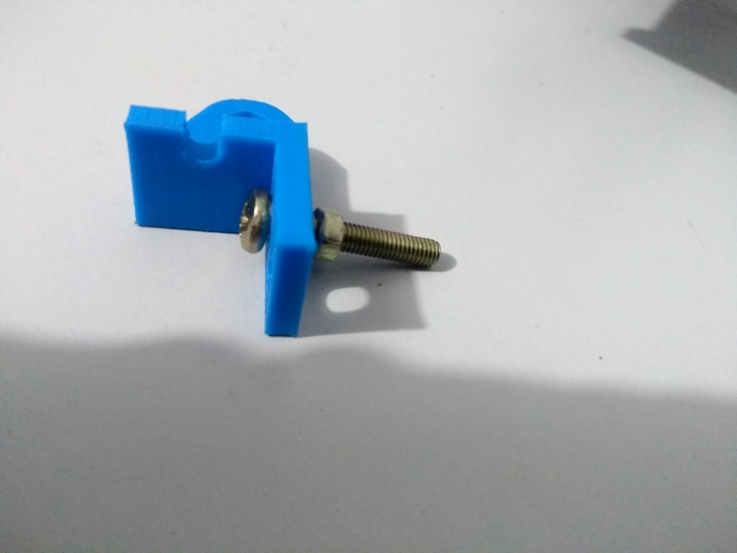
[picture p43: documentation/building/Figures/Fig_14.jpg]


We put both in the 2 profiles, adjusting them with nuts

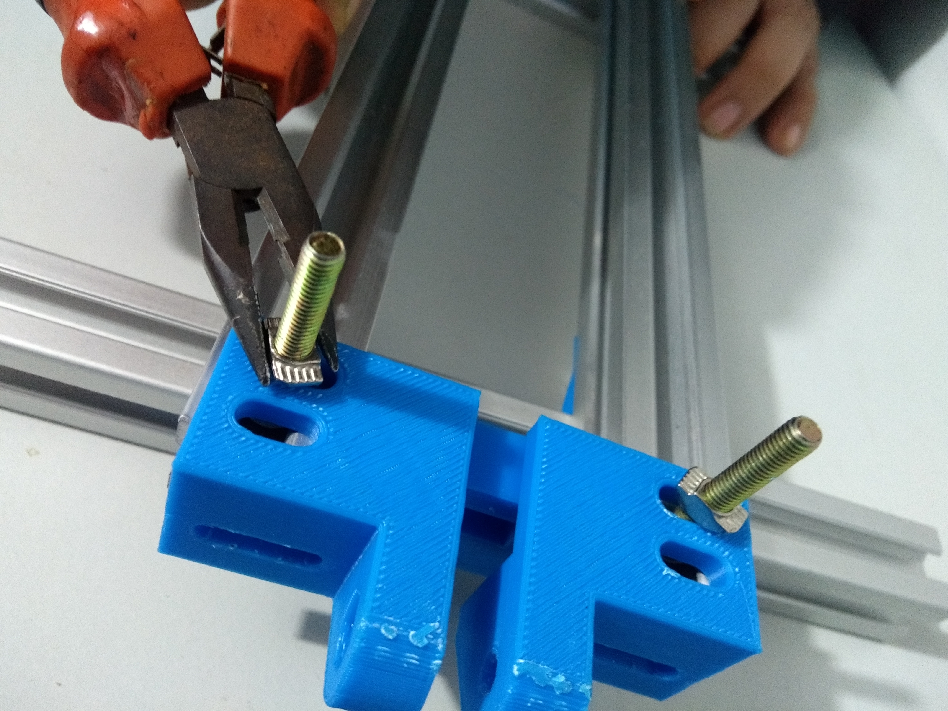
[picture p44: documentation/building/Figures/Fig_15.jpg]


then we enter the pulley and place it with the M5

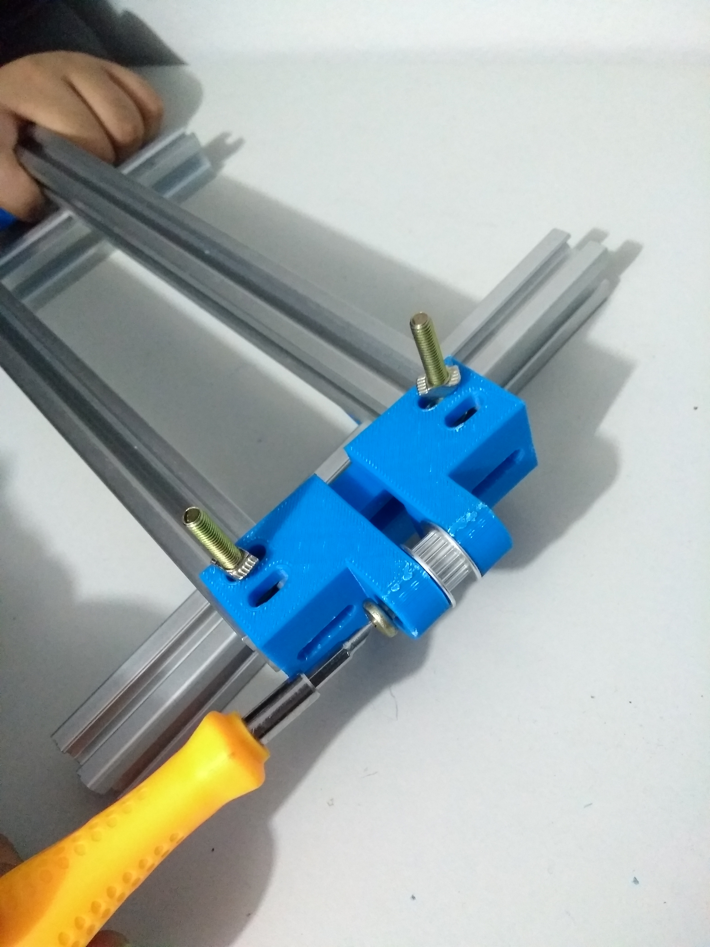
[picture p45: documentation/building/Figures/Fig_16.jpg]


Now we go to the other side of the profiles and place the 3d printed motor support

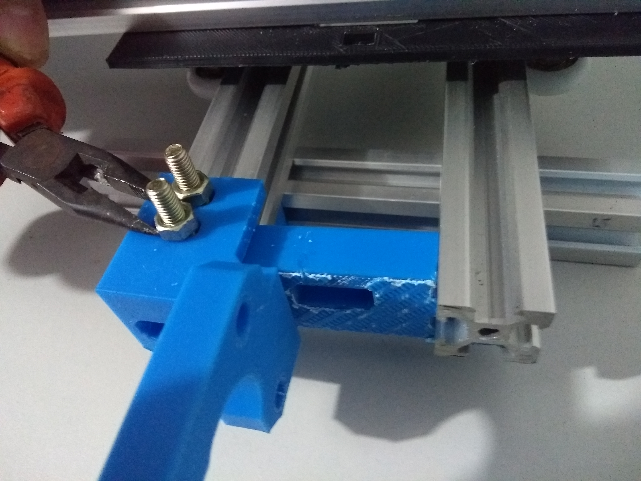
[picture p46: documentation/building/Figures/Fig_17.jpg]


then we place the motor and adjust with its respective bolt

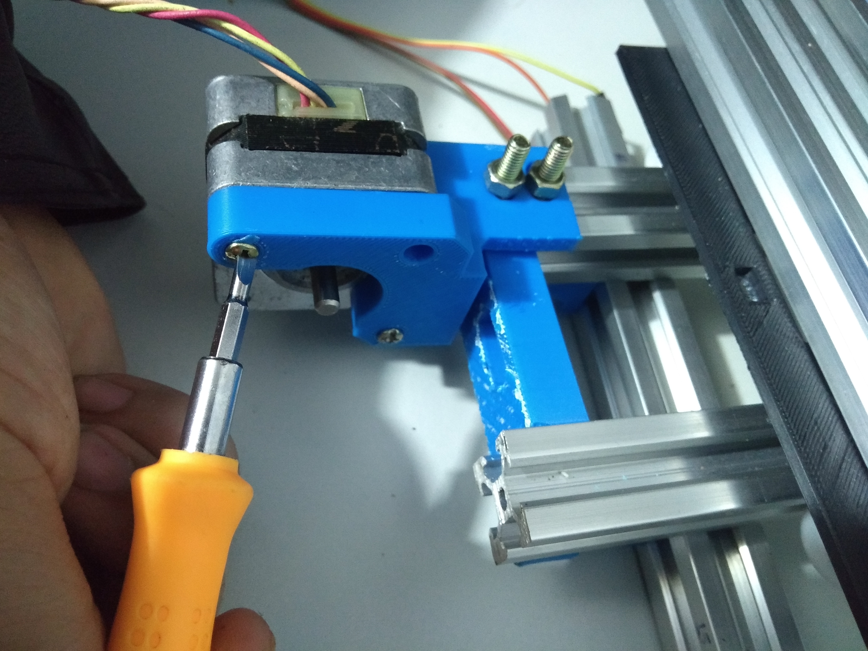
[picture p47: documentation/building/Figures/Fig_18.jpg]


we put the pulley timing to the motor

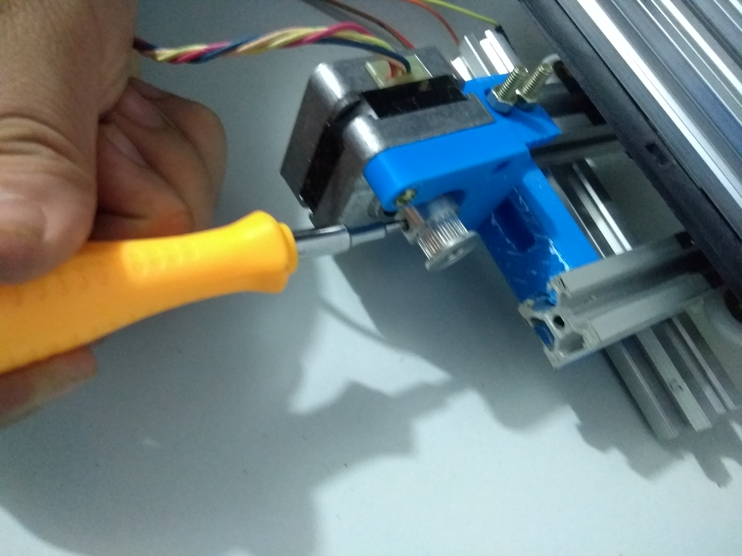
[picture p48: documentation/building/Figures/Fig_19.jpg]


Now we place the timing belt and adjust on both sides with a cable tie

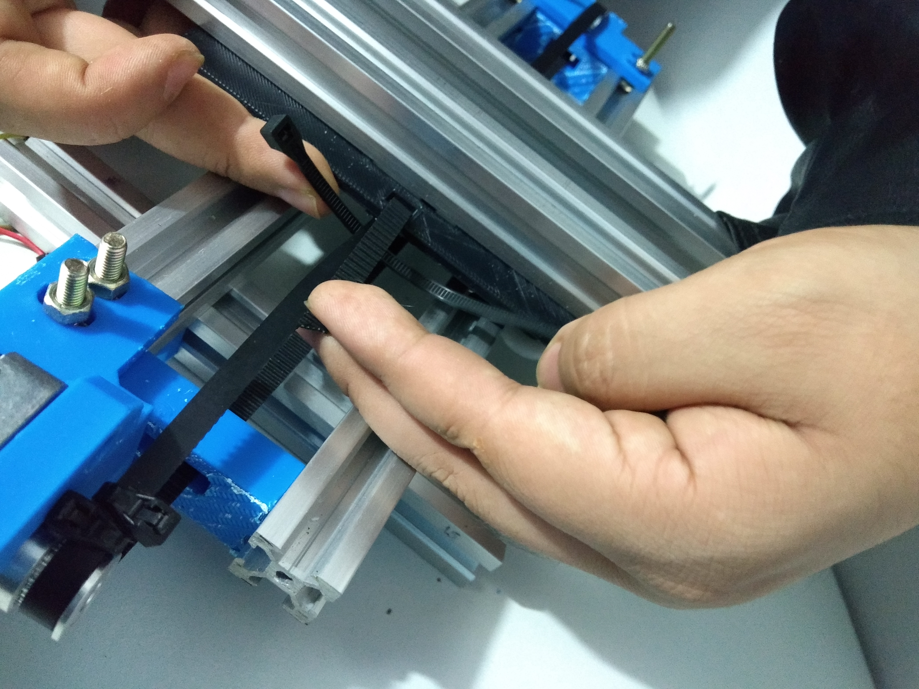
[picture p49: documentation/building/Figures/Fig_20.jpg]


now we turn the equipment and use a profile separator between the other two profiles to align the profiles 

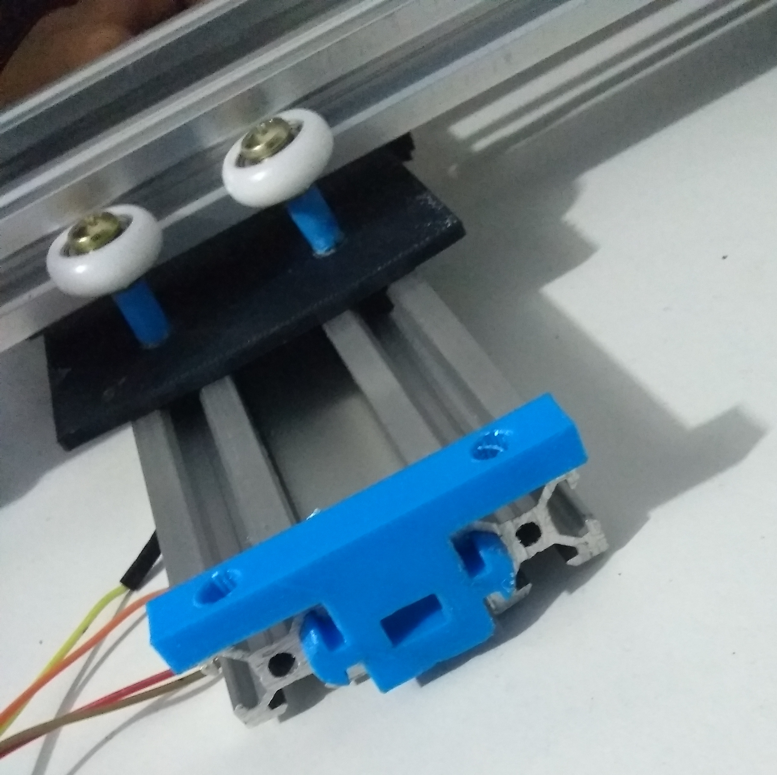
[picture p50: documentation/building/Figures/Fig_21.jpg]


adjust with the corresponding nut

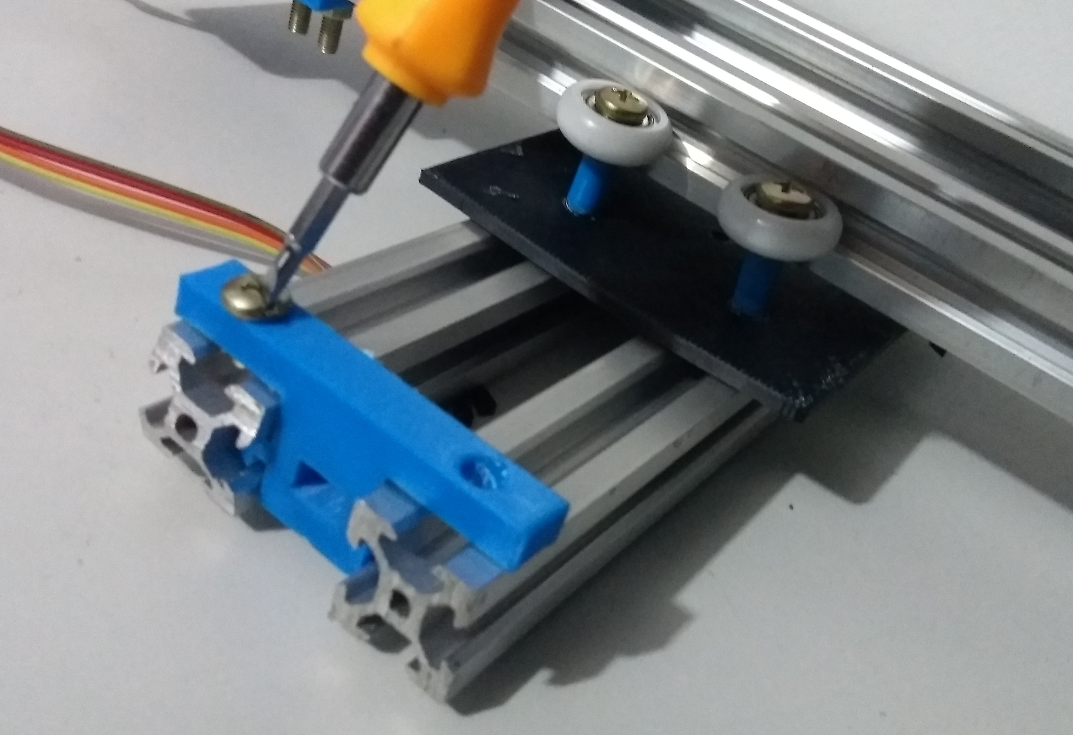
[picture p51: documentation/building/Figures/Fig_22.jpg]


Full view until now
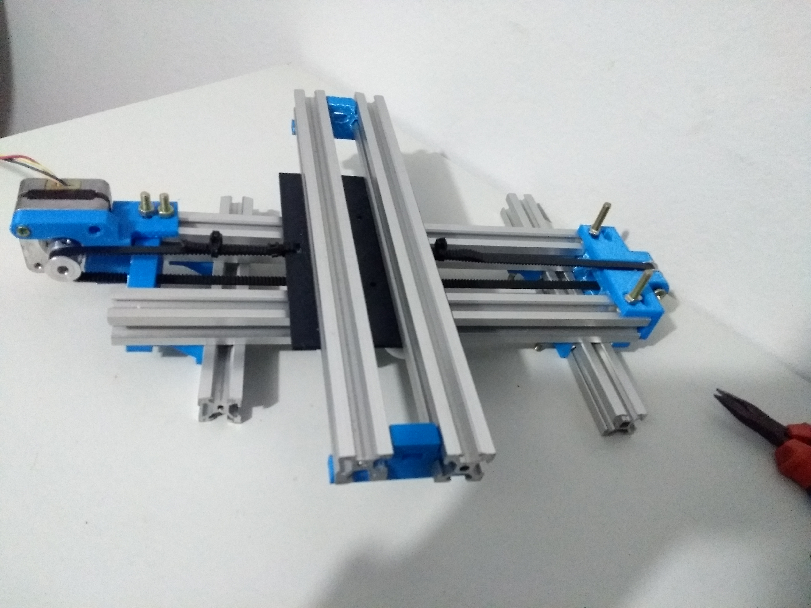
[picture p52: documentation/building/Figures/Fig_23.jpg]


**3. Building the Y axis plate:**

Take the M5x30mm bolts and put it in a nylon wheel and adjust it with its corresponding nut

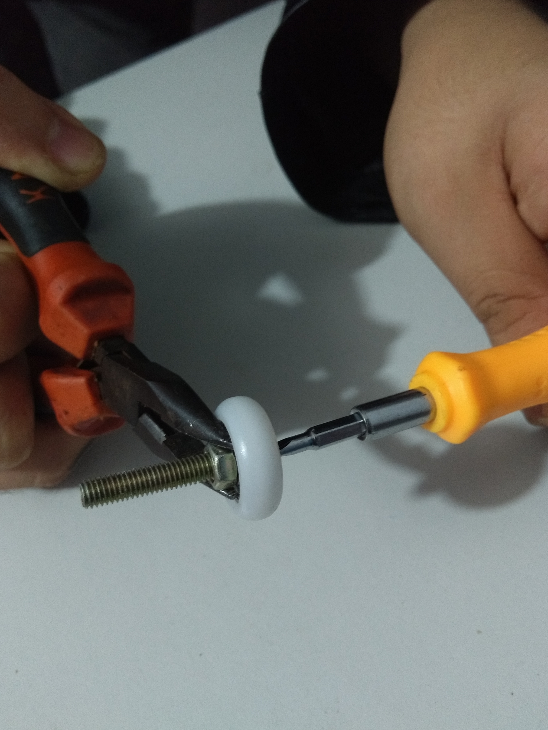
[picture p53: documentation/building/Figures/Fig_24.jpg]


We take the printed cylinders and put it after the nut

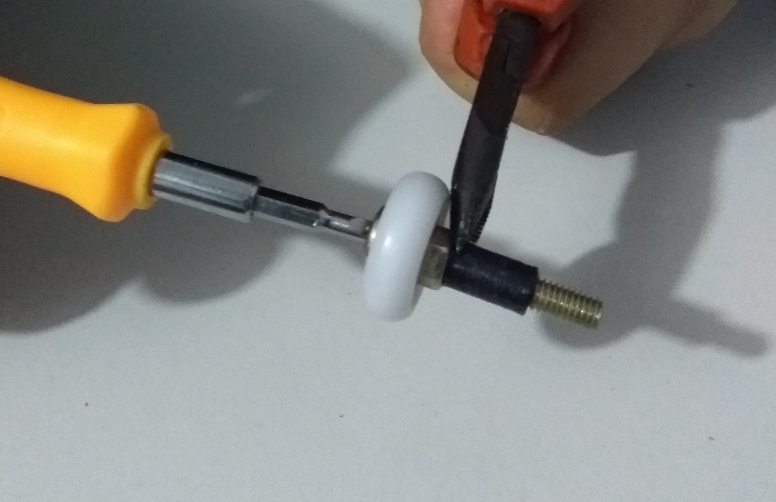
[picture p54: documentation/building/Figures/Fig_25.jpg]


Then, we insert this piece inside one of the wholes of the base of the Y axis plate , and repeat for the 4 wheels 

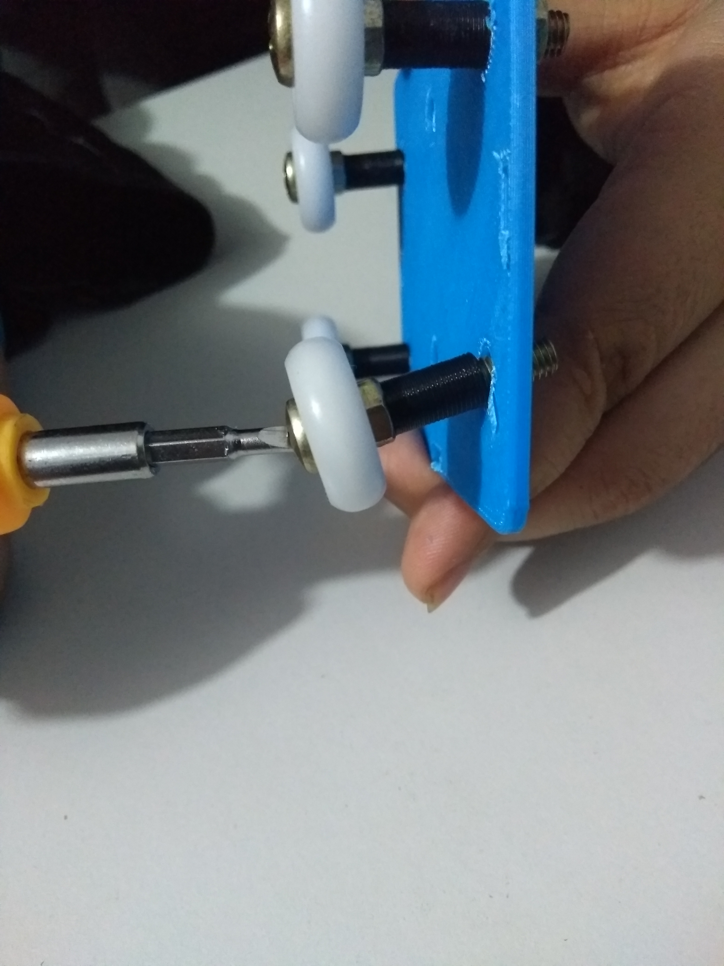
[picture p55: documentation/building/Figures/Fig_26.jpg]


adjust with the corresponding nut

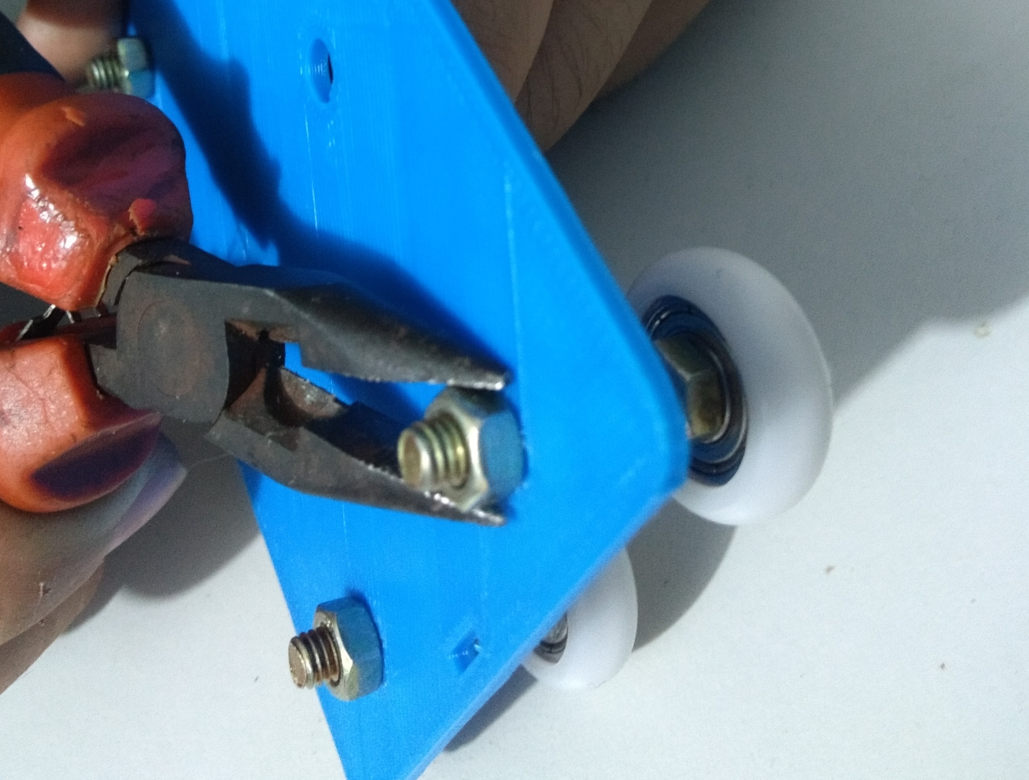
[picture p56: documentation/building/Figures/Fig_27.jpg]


top view of the plate

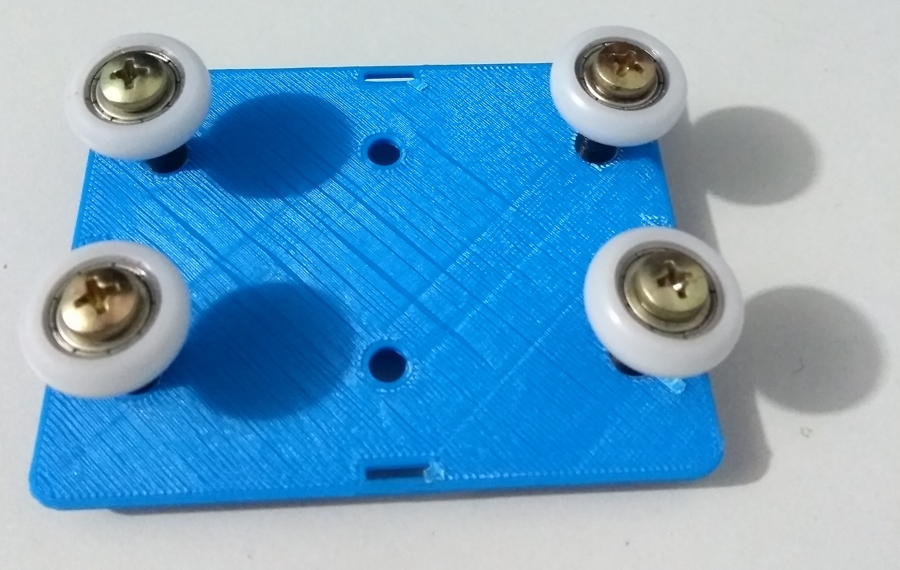
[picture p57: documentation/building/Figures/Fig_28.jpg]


Bottom view of the plate

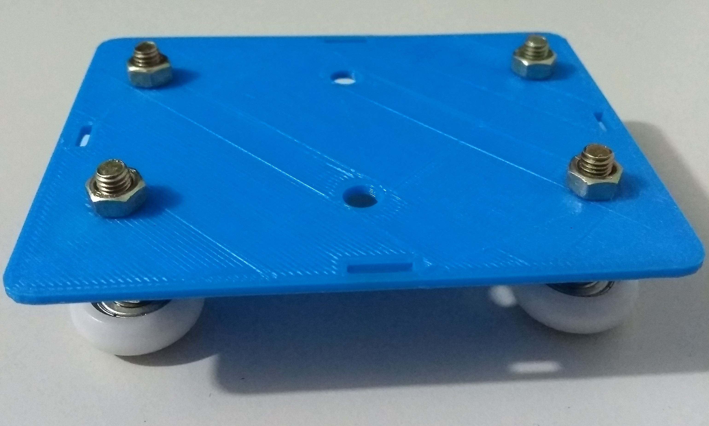
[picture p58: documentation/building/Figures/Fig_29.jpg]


as in previous steps we place the left and right belt adjuster with nuts

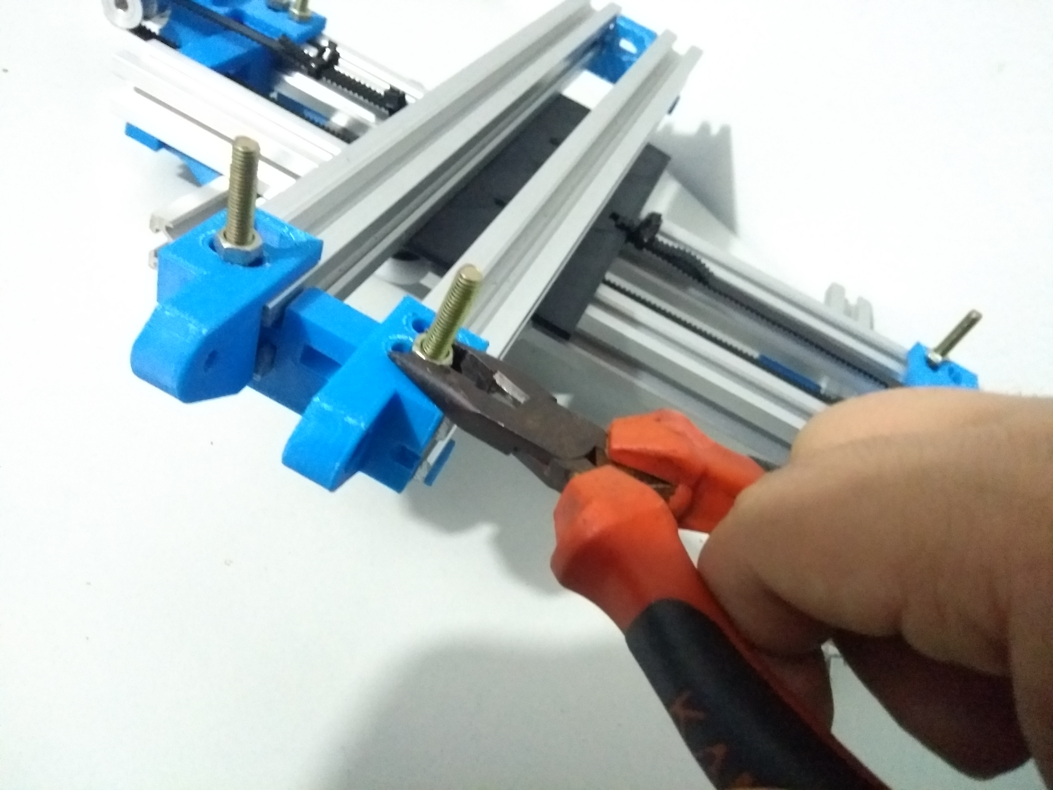
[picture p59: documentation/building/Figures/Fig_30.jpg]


then we enter the pulley and place it with the M5

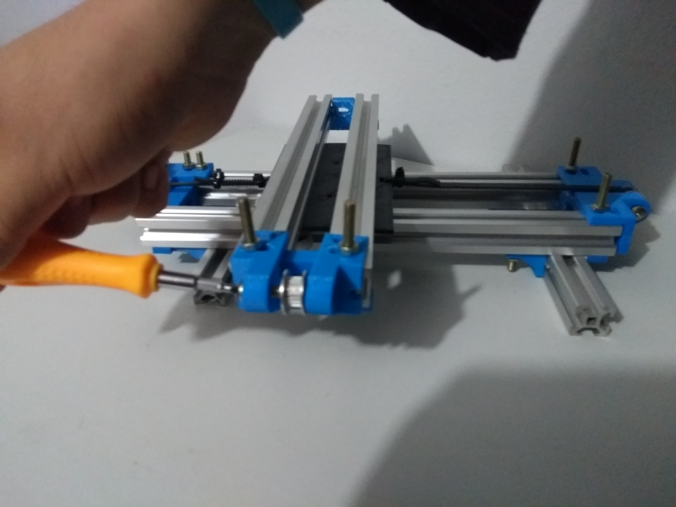
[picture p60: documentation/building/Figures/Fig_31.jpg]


Then, we enter the plate of the Y axis previously assembled on the rail 

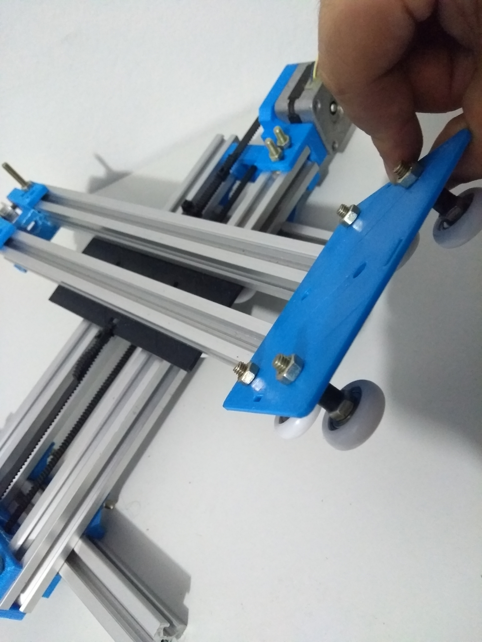
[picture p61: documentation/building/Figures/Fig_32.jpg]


Now we go to the other side of the profiles and place the 3d printed motor support

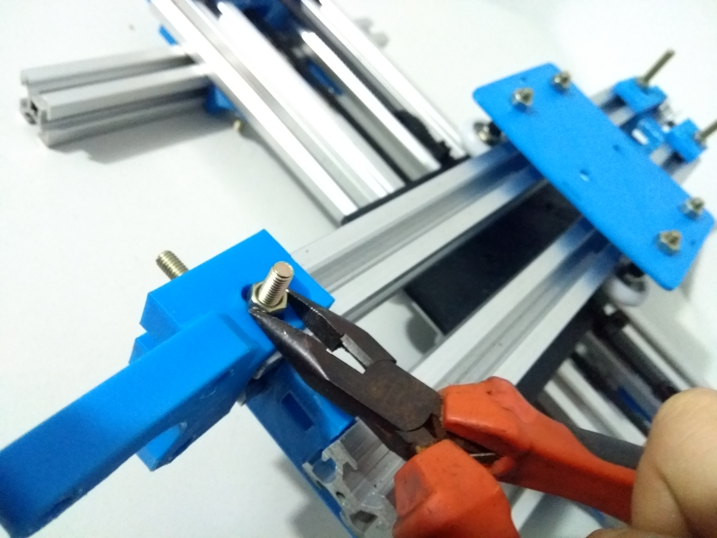
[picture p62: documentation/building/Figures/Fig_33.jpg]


adjust with the corresponding nut

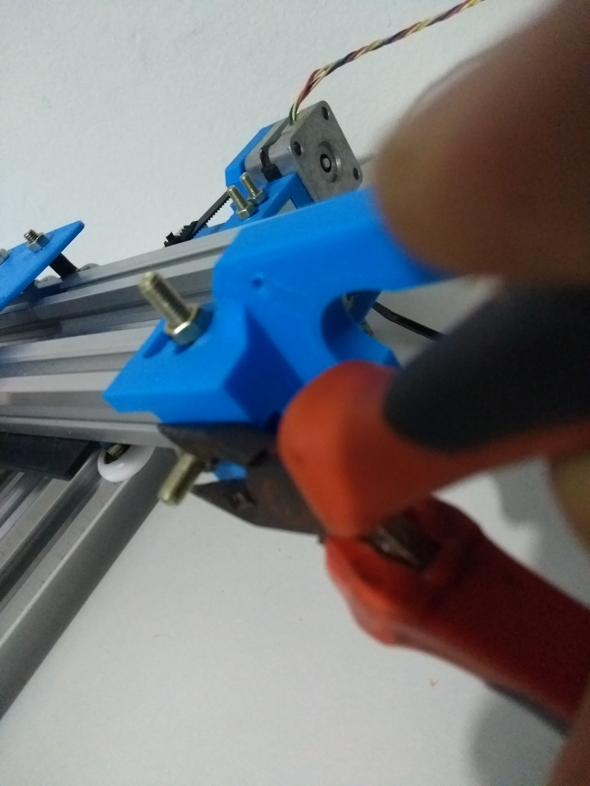
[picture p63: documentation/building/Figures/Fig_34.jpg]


then we place the motor and adjust with its respective bolt

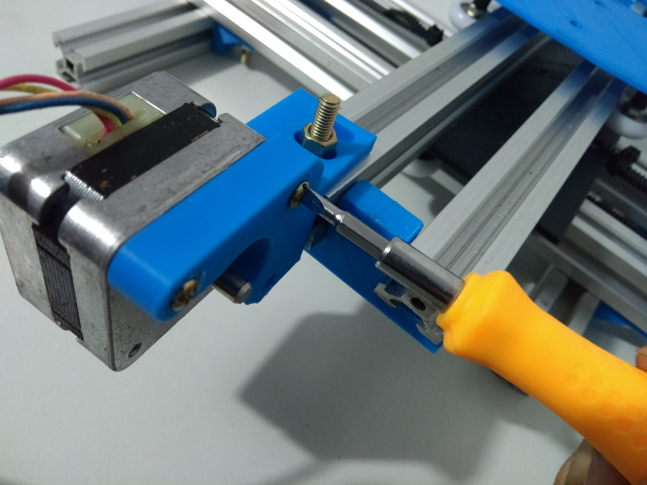
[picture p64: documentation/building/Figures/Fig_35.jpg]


we put the pulley timing to the motor

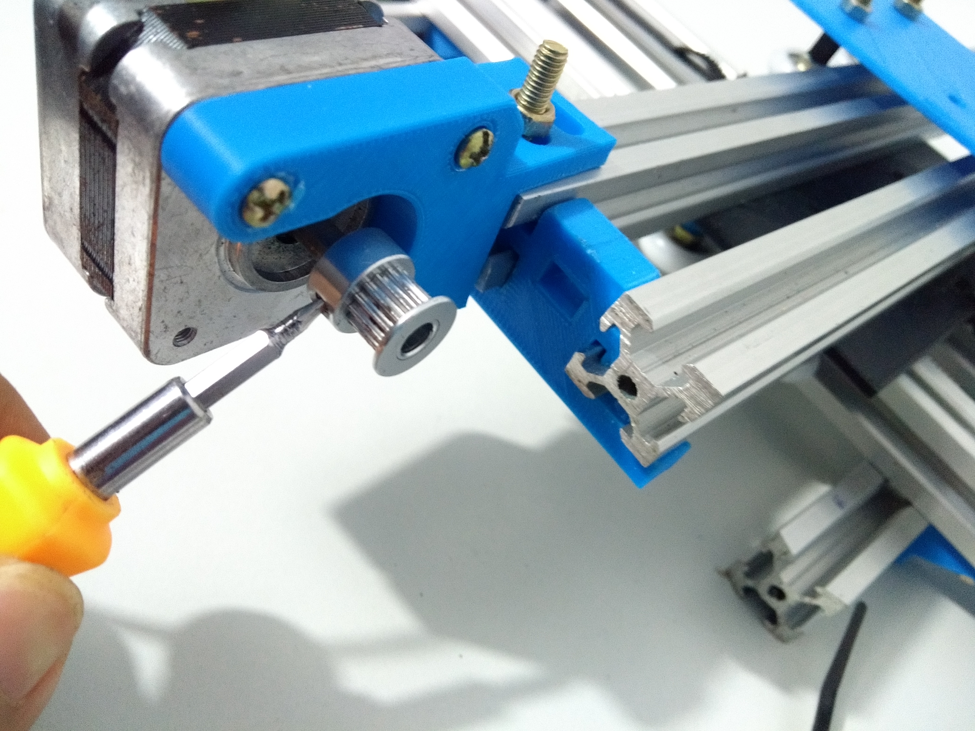
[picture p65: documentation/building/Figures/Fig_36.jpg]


Now we place the timing belt and adjust on both sides with a cable tie



full view with the 2 complete axes

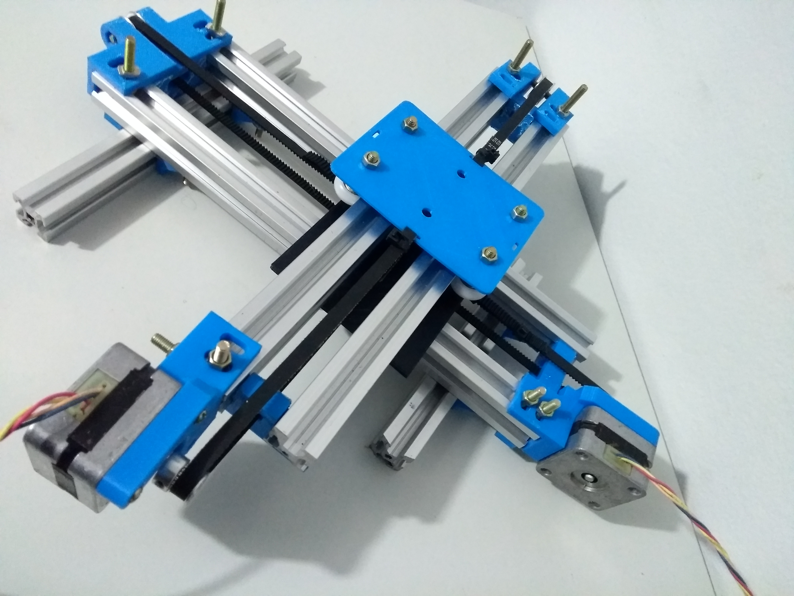
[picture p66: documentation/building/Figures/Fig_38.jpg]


**4. Building the Z axis:**

we will use the lead screw with its mount, we adjust with its nut

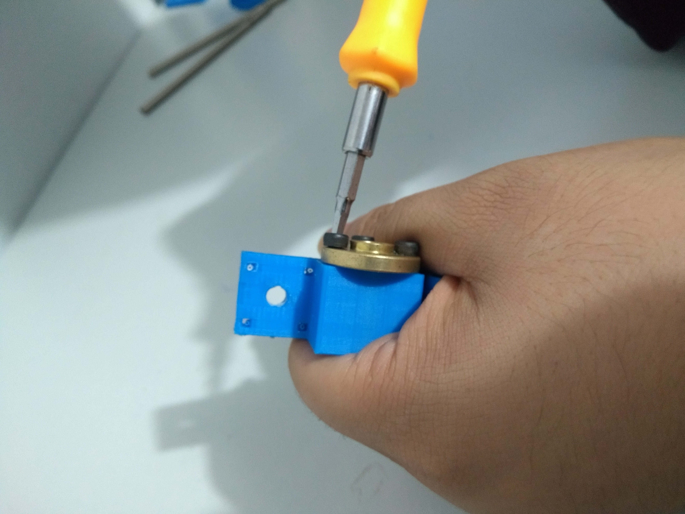
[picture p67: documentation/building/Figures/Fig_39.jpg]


we introduce the 2 bolts to hold the piece
 
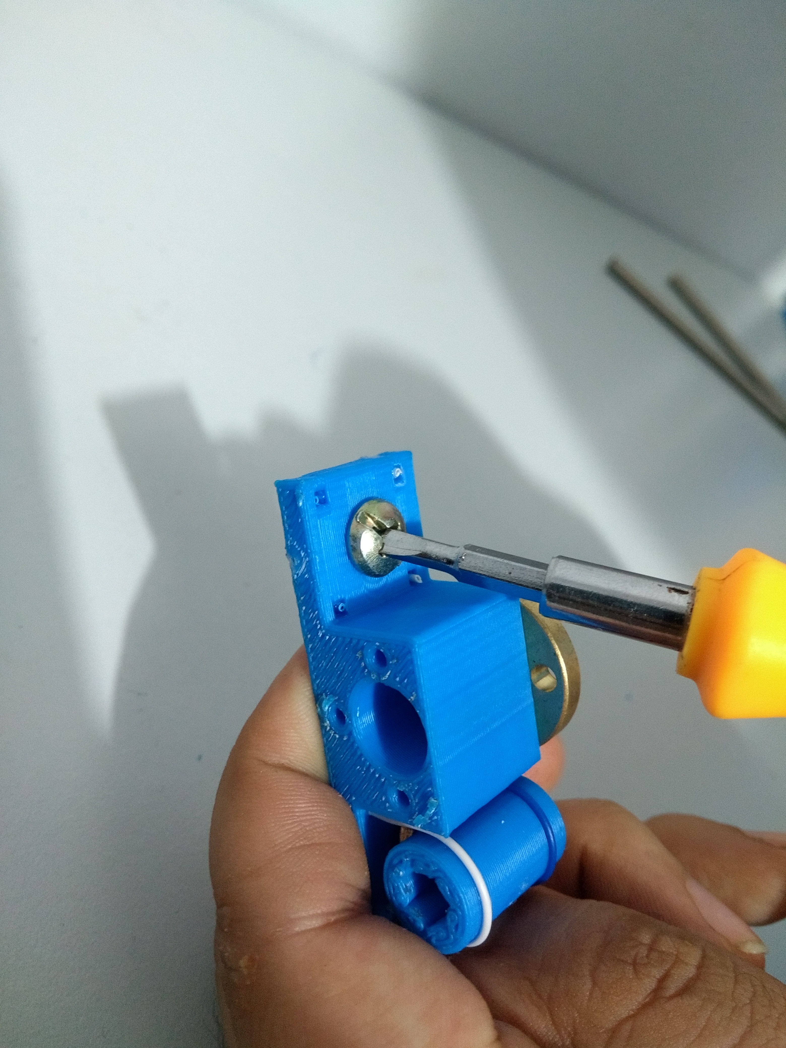
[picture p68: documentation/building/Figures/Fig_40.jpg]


for this case we will use 6mm steel rods and linear rod bearing printed in 3D with this measure



We introduce the rods to the linear rod bearing



In the same way we have a piece printed in 3d to place a ball bearing



Place the pieces to fit on both sides of the rod



how the complete structure would look



we introduce all this structure in a support piece that constitutes the z-axis



we place the motor on the shaft



we enter an 8mm screw



we put a shaft coupling to join the motor with the screw



once we have all the complete piece we join everything to the Y axis plate and adjust the nuts



full view of the Z axis



**5. Adapting the needle with the servo:**

We use the servo support and we adjust it to the part that is attached to the lead screw



we enter the servo and adjust with their corresponding bolt



we put the servo arm and adjust



we have a piece printed in 3D designed for hoses of 3mm, which we enter and join the needle (with its lid placed for security)



we join this piece with the servo arm adjusting with its screw



view of the servo attached to the servo



This how the 3 assembled axes look



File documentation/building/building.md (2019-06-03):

**Use this folder to create files for building instructions:**
- Each equipment is going to have a different building process, but here are some suggestions on how to organise things:

<br>

1. getting started:
  A micromanipulator is an equipment that allows the user to manipulate things in a microscopic level. Here we show how to build an open source micromanipulator from scratch. In order to accomplis this, you will need to know basic electronics, how to program an Arduino, basic 3D printing skills. 
  This is safe for amateurs although we do not recommend it for kids since a needle will be involved in the process and kids might get hurt. One person can perfectly build this equipment by him/herself. 
  Average time to build: --- 
In case something goes wrong, please do not hesitate in contacting us at dulce.alarcon@upch.pe and jean.tincopa@upch.pe
<br>

2. List of materials needed:
 - In the form of a table, containing part name, quantity and a couple of words on what they do. Extra points if the parts are divided according to the building steps (below)
 - Remember to include the tools necessary as well! (pliers, saw, computer, etc)  

 |part name| function  | quantity  | build step  | obs.  |
 |---|---|---|---|---|
 |LM2596| voltage regulator  | 2  | 3  | these could be substituted by XX  |
 | Nose needle Pliers  | hold components while soldering  | 1  | all steps  | regular pliers would also work  |

<br>

3. build steps:
 - Divide this section in as many subparts as you like and try to be as clear as possible. Would someone seeing the whole thing for the first time be able to build it? (it is a good exercise to oversee someone building the equipment using only your written/video/figure instructions)
 - Is a video a better way to instruct people how to use it? try to keep the file size as small as possible without compromising quality. Also reach out to us, as a good idea might be to create a different repository for the video files.  

<br>

4. Last checks before powering up/using for the first time:
 - Could people do one more check of everything before powering up things? Maybe double check that the capacitors were soldered in the proper orientation? Make sure there are no cut metal parts shorting the bottom side of the PCB? Make sure the area around the equipment is clear and won't be hit if the equipment has moving parts (eg shakers, centrifuges, etc).

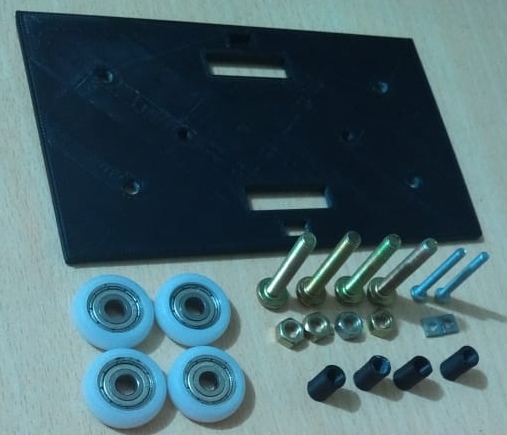
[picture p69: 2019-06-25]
documentation/building/Figures/Partes_plato_X.jpg

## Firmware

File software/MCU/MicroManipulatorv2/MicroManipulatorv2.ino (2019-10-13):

#include <AFMotor.h>
#include <Servo.h>

AF_DCMotor motor(3), motor2(4),motor3(2),motor4(1);
int ledPin = 13; 
int Jx = 0;
int Jy= 0;
int Jz= 0;
Servo myservo; 
int pos=0;
int pump =A3;

void setup() {
  myservo.attach(10);
  Serial.begin(9600);
  pinMode(ledPin, OUTPUT);
  digitalWrite(ledPin,LOW);
  motor.setSpeed(100);
  motor.run(RELEASE); 
  motor2.setSpeed(100);
  motor2.run(RELEASE);
  motor3.setSpeed(100);
  motor3.run(RELEASE);
}

void loop() {
     
  motor.setSpeed(155);
  motor2.setSpeed(155);
  Jx = analogRead(A0);
  Jy = analogRead(A1);
  pump=analogRead(A2);
  Jz = analogRead(A3);

  Serial.print(Jx);
  Serial.print(" , ");
  Serial.println(Jy);
  Serial.print(" , ");
  Serial.println(Jz);
  delay(10);
  
  if (Jx>650)
  {Serial.print("Der");
  motor.run(FORWARD); motor.setSpeed(205);
  digitalWrite(ledPin,HIGH);delay(10);}
    else if(Jx<250)
  {Serial.print("Izq");
  motor.run(BACKWARD); motor.setSpeed(205);  
  digitalWrite(ledPin,HIGH);delay(10);}
    else
  {digitalWrite(ledPin,LOW);delay(10);}

  if (Jy>650)
  {Serial.print("Aba");
  motor2.run(FORWARD); motor2.setSpeed(205);
  digitalWrite(ledPin,HIGH);delay(10);}
    else if(Jy<250)
  {Serial.print("Arr");
  motor2.run(BACKWARD); motor2.setSpeed(205);  
  digitalWrite(ledPin,HIGH);delay(10);}
    else
  {digitalWrite(ledPin,LOW);delay(10);}

  if (Jz>650)
  {Serial.print("Aba");
  motor3.run(FORWARD); motor3.setSpeed(205);
  digitalWrite(ledPin,HIGH);delay(10);}
    else if(Jz<250)
  {Serial.print("Arr");
  motor3.run(BACKWARD); motor3.setSpeed(205);  
  digitalWrite(ledPin,HIGH);delay(10);}
    else
  {digitalWrite(ledPin,LOW);delay(10);}

  motor.run(RELEASE);
  motor2.run(RELEASE);
  motor3.run(RELEASE);
  
 
  if (pump>250)
  {myservo.write(45);delay(10);}
  
  else if(pump<650)
  {myservo.write(120);delay(10);}
  
  else
  {delay(10);}


  
}
